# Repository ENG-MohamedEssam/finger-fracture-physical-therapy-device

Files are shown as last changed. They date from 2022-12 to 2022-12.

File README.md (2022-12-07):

# finger-fracture-physical-therapy-device

#### Note that this whole project was made by me from the Reverse-Engineering phase to the design to the fabrication of the final product

## **Abstract**

#### This project was for helping the physical therapist to help aid the patiets that had a broken or fractured finger
#### The device mainly uses a potentiometer to send the data of the the finger's angle to LCD and to the phone through a bluetooth module
#### The device has Arduino Nano as it's main controller, Potentiometer to send the Angle Data, LCD to show the data, Bluetooth module to send the data to the phone , 2 push buttons one for the hold of the readings, the second is for getting the angles in degree and minute format

#### The project went throgh four phases

## Phase 1 Idea
#### The idea was to replicate the behaviour of a digital protractor device that was already in the market to invent something that may help the patients with broken fingers
## Phase 2 Reverse-Engineering
#### So i started Reverse-Engineering the Digital protractor as shown below 
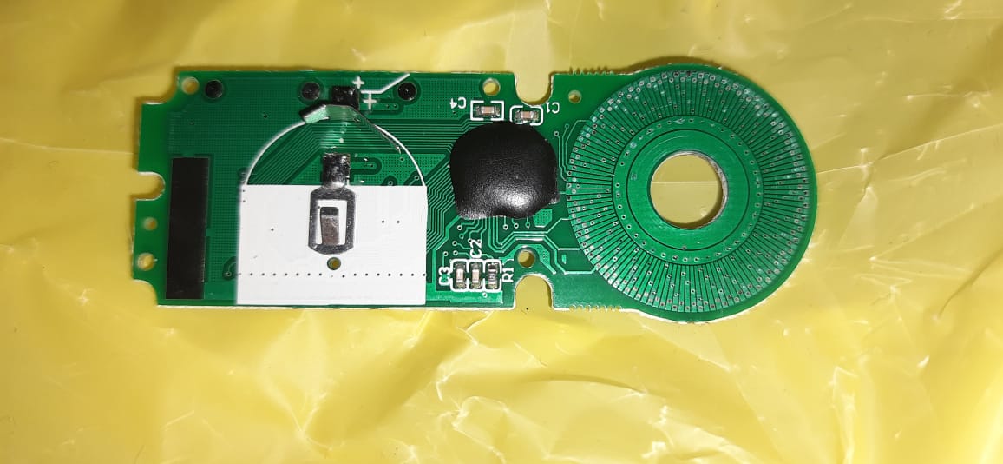
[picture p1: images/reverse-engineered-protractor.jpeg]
protractor

#### When i understood it's behaviour i started to find similar components in the Egyptian market 
#### the components that i didn't find was the induction encoder so i had to find a replacement
#### i thought of three things, Potentiometer, Normal Encoder, IMU
#### I even wrote codes for the three sesors.
## Problems 
#### IMU was too expensive for such a project but it kind of worked correctly
#### The encoders in Egypt had too little pulses so the error in Degrees was not acceptable
#### The potentiometer was the cheapest sensor so in mass production that was the ideal choice but it gave an error in the reading as well that was not acceptable and the Arduino Nano was only 10 bits in ADC

## Scenario to fix the Potentiameter's problem
#### To fix the problem in the potentiometer there were two solutions either i use the algorithm over sampling and decimation or i use the sliding window filter
#### so i went along with the over sampling and decimation technique, it was by having many readings in an array then get the average of it many times, that makes the reading more accurate.
#### The error after that algorithm was +/- 0.02 and that was more than acceptable.

## Phase 3 Design
#### In this phase i started to design the circuit on protues such as follows
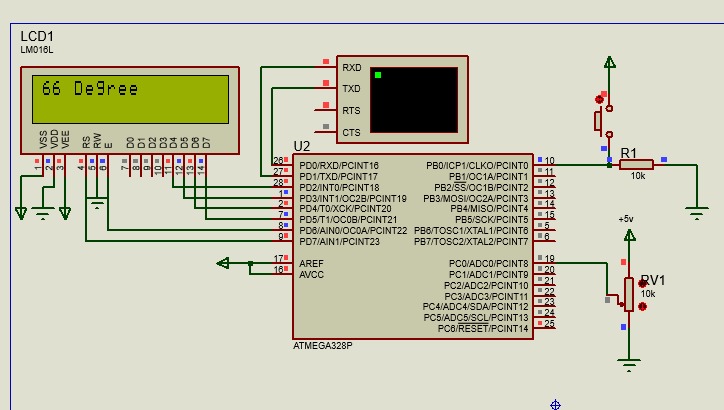
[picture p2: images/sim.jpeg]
sim

#### After i made sure it works fine i turned to try the components connections on a bread board as follows 
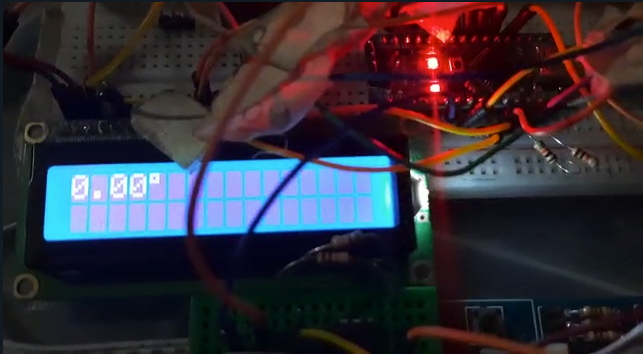
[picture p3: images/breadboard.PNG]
breadboard

#### Then i designed the circuit on Eagle-Cad program 
#### I even designed one of the three parts on SolidWorks as you can see below 
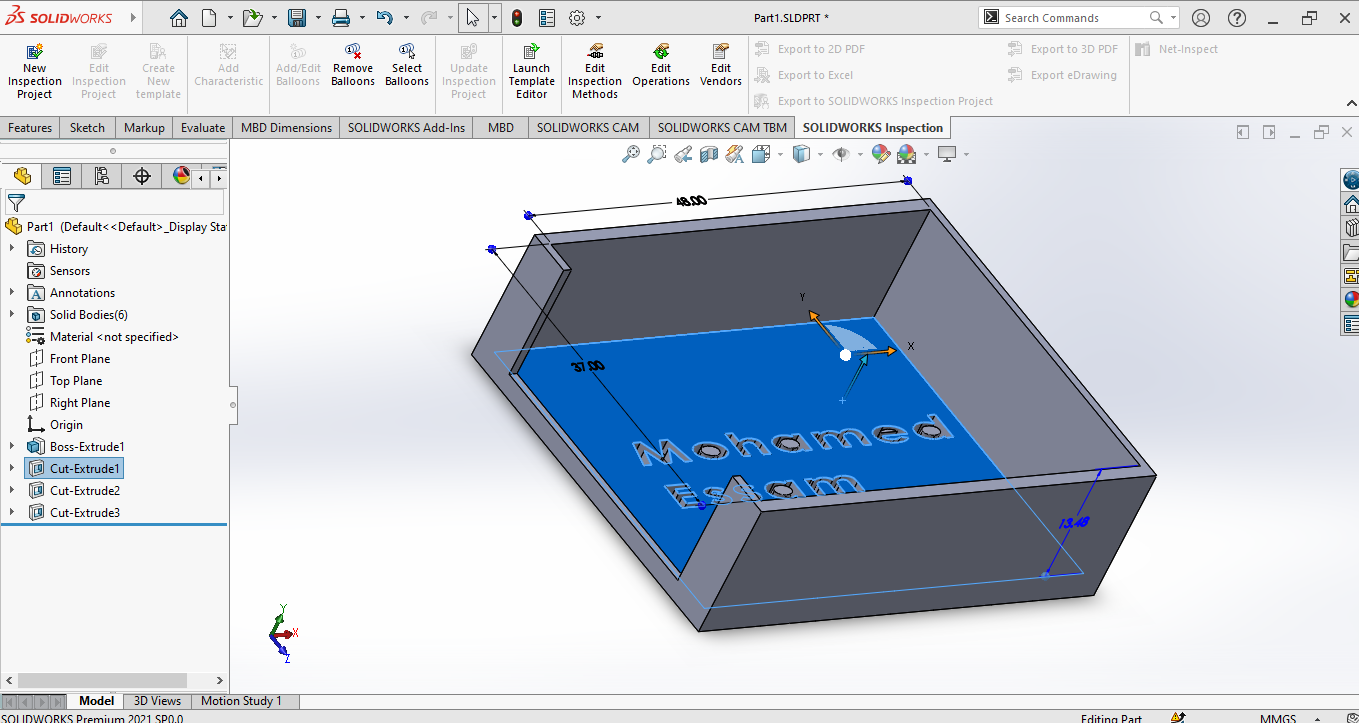
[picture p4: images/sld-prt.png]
Part

#### the other two parts were open source 

## Phase 4 fabrication
#### in this phase i fabricated the PCB and tested it and it worked fine, below are some images of the final product (The band)
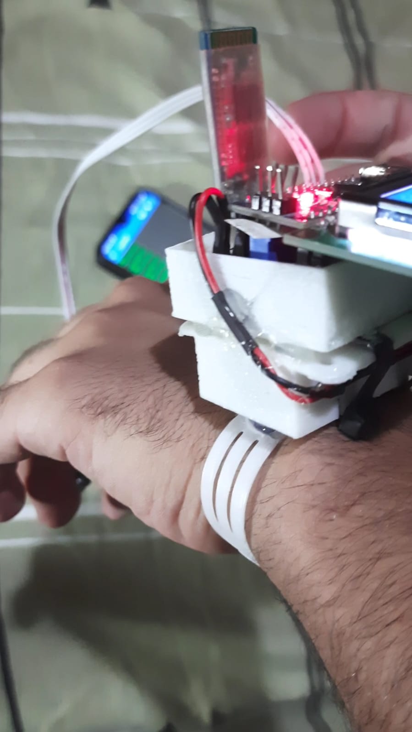
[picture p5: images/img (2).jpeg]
band-img1

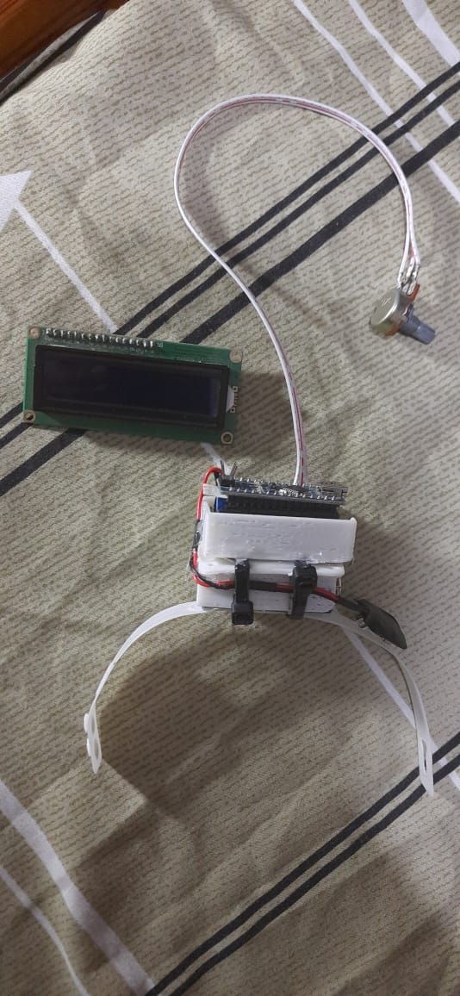
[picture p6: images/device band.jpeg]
band-img2

#### The following is a video of me explaining how the whole process works
[Explanation](https://drive.google.com/drive/folders/1u0ruocD8NN2b_IU45vWWJVkj_FHNx0_M?usp=share_link)

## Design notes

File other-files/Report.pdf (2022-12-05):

# Finger Fracture Physical Therapy Device

# Report

Name : Mohamed Essam Abd Elfattah Ibrahim.
ID : 148
Department : Electrical Power and Machines Engineering.

## This project was made under the supervision of :

## Dr. May Youssef

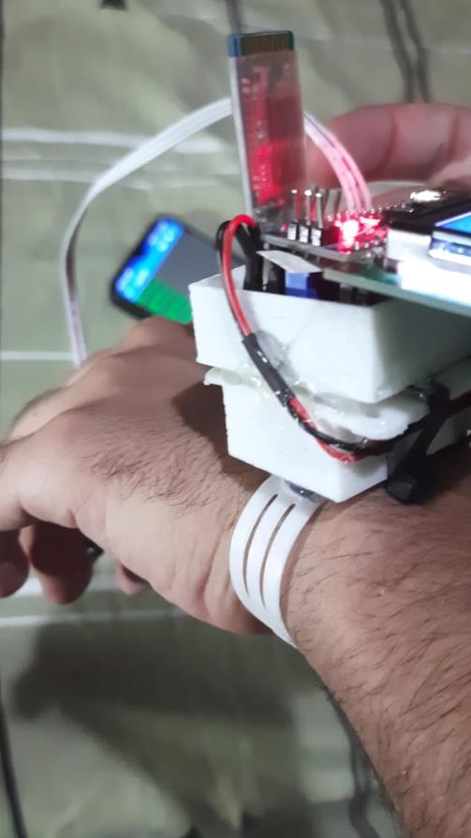
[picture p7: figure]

## Dr. Mohamed Elhabrouk

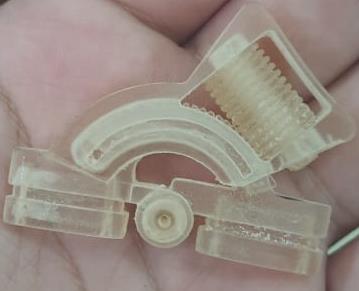
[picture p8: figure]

## Idea :

The main idea of the project was to replicate the functionality of a Digital Protractor to use it as a Physical Therapy device, by enhancing its behavior and precision in order to use it in the medical field.

## Functionality:

It’s used for physical therapy on figure fractures, It helps the Physical Therapist to read the angle and that helps him to treat the patient effectively.

## Progress:

First was the reverse Engineering process

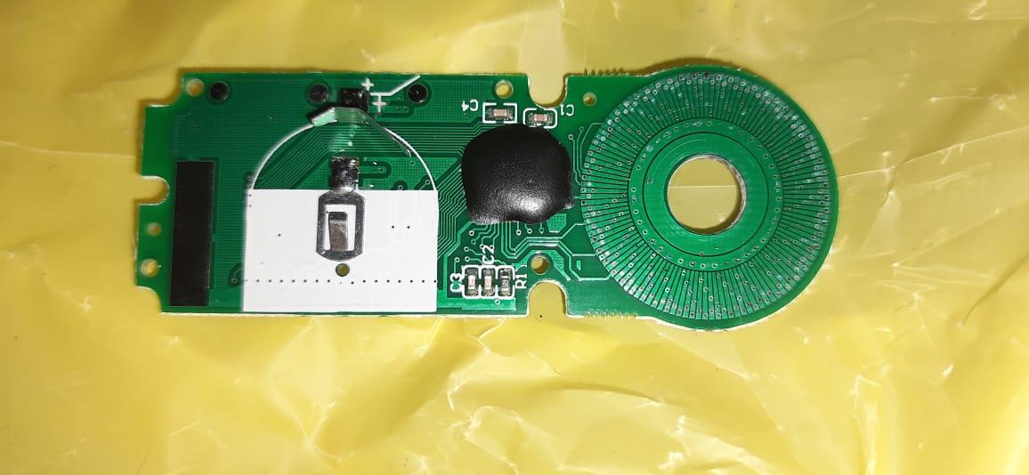
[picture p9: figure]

I was able to find out the inputs and outputs of the Digital Protractor and every sensor and component used to make it.
The main components that were inside the Digital Protractor :
- Micro-Controller
- 5 Bit LCD screen
- Inductive Position Encoder
- Switches
- 3v Battery

The main components which I used were :

- Micro-Controller (Arduino Nano)
- 16x2 LCD character screen
- Bluetooth Module (HC-05)

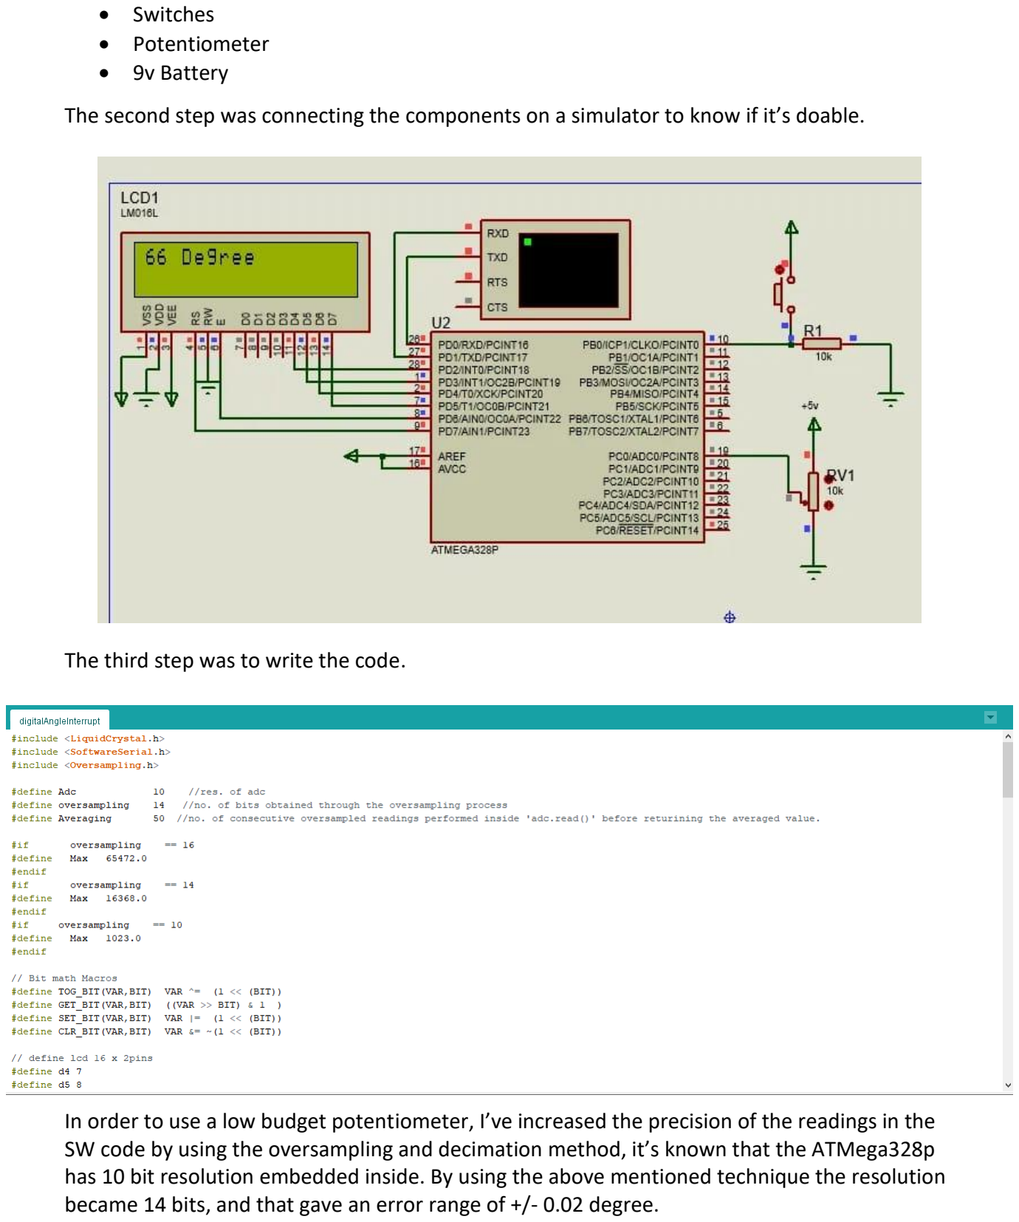
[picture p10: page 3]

- Switches
- Potentiometer
- 9v Battery

The second step was connecting the components on a simulator to know if it’s doable.

The third step was to write the code.

In order to use a low budget potentiometer, I’ve increased the precision of the readings in the SW code by using the oversampling and decimation method, it’s known that the ATMega328p has 10 bit resolution embedded inside. By using the above mentioned technique the resolution became 14 bits, and that gave an error range of +/- 0.02 degree.

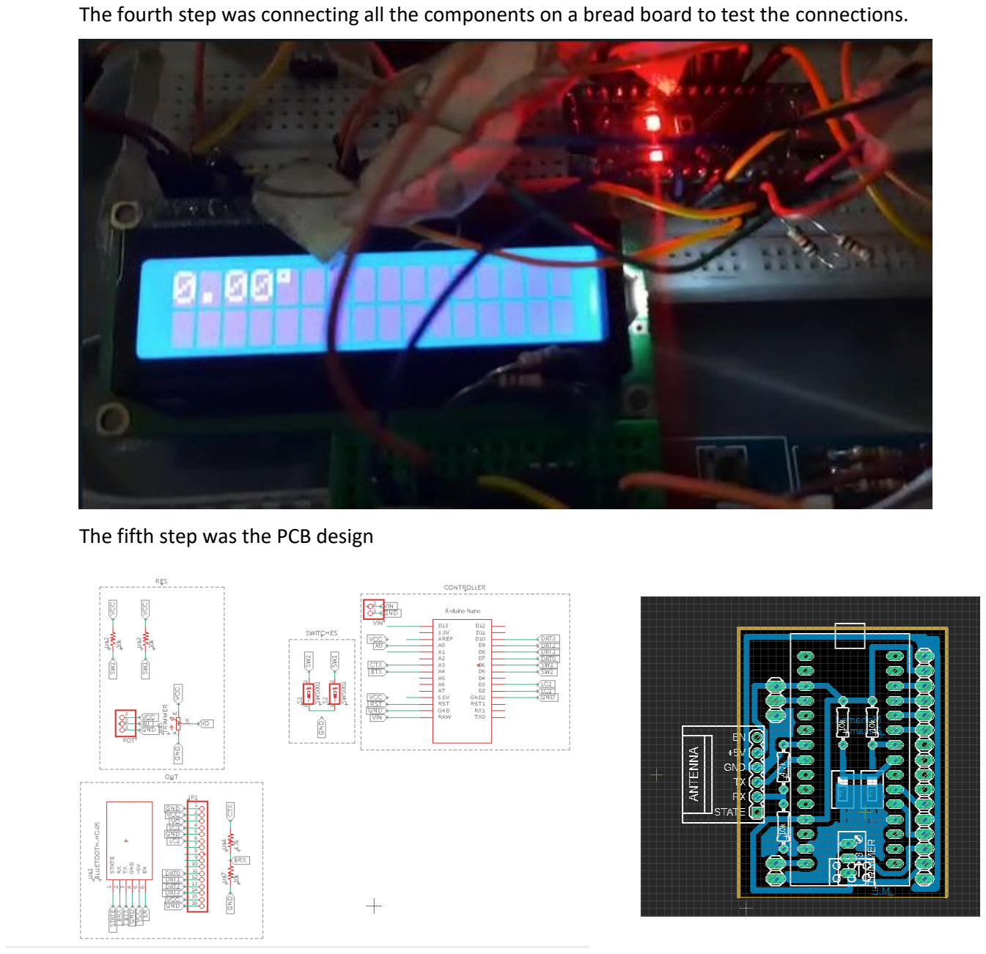
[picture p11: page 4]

The fourth step was connecting all the components on a bread board to test the connections.

The fifth step was the PCB design

The Last step was to fabricate the PCB and connect all the components on it to make it compact.

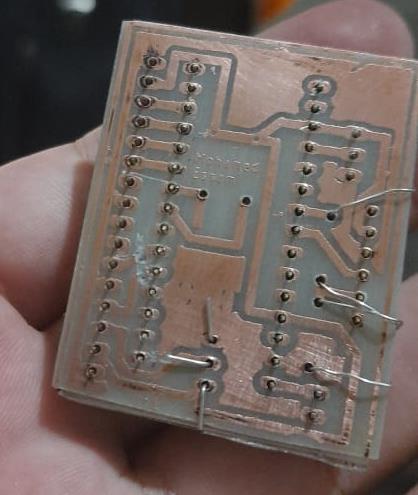
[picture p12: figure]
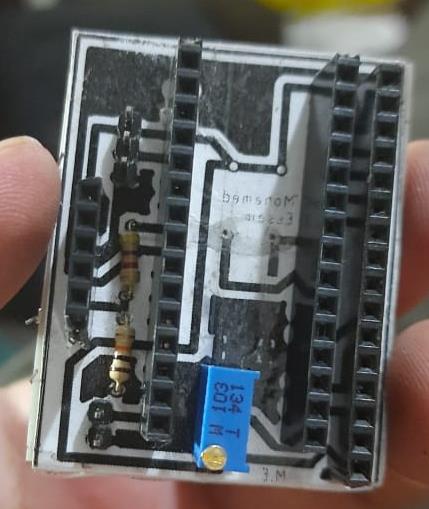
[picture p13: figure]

The final Product was a fully functioning PCB as shown in the figure below :

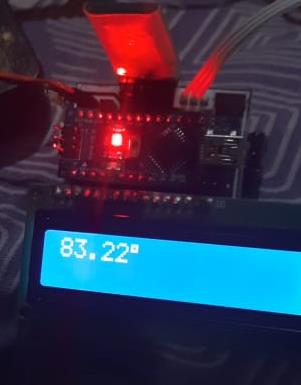
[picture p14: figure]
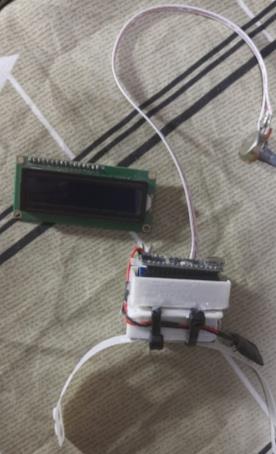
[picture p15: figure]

And by adding 3d printed parts the project became as shown:

## Features :

The project has many features, such as :

The precision that was mentioned before.

It sends the reading to an LCD and through Bluetooth module into any Bluetooth serial terminal Application on the mobile phone.

It has a switch that can Hold the reading.

Also another switch that toggles between the reading in degree with fraction and the reading in degrees and minutes.

It has a low cost Potentiometer.

It has a small sized PCB that can be put on the hand like a wrist-band.

## Future Improvements:

- Using ATMEGA328p Controller’s Chip instead of the full Nano Platform
- Using a smaller sized Bluetooth-Module
- Using a 4 digit LCD instead of 16x2 LCD to make it smaller
- Using a better quality Potentiometer
- Using a rechargeable small sized LI-PO Battery

## Notes:

The Potentiometer used is a low quality one, that’s why the Angle may be shifted by 2 to 5 degrees from the real angle depending on the potentiometer, and that can be fixed in the code using the mapping function and by getting a better-quality Potentiometer.

# Bill of Materials (BOM)

Component | Price | Quantity | Total Price | Link
Arduino Nano | 175 | 1 | 175 | https://makerselectronics.com/product/arduino-nano
16x2 LCD | 50 | 1 | 50 | https://makerselectronics.com/product/16x2-character-lcd
Bluetooth Module | 160 | 1 | 160 | https://makerselectronics.com/product/bluetooth-module-hc-05

PCB | 6 | 1 | 6 | https://makerselectronics.com/product/pcb-board-fiber
Trimmer | 3.5 | 1 | 3.5 | https://makerselectronics.com/product/multi-turn-pot-20k
Pot | 3 | 1 | 3 | https://makerselectronics.com/product/pot-1m
Switches | 1 | 2 | 2 | https://makerselectronics.com/product/push-button-3x6x5-0mm
Resistors | 0.1 | 4 | 0.4 | https://makerselectronics.com/product/resistor-1-2ohm-1-2w
9v Battery 6F22 | 15 | 1 | 15 | https://makerselectronics.com/product/camelion-battery-9v-6f22
Battery Cap | 1.5 | 1 | 1.5 | https://makerselectronics.com/product/battery-9v-cap
Pin header female | 3 | 2 | 6 | https://makerselectronics.com/product/pin-headers-female-40-pins
Pin header male | 2 | 1 | 2 | https://makerselectronics.com/product/pin-headers-male-40-pins
Data Cable 3 pin | 5.5 | 1 | 5.5 | https://makerselectronics.com/product/data-cable-jst-3-pin-30cm
19 grams of filament PLA+ | -- | -- | --

# Project Total Cost : 429.9 EGP

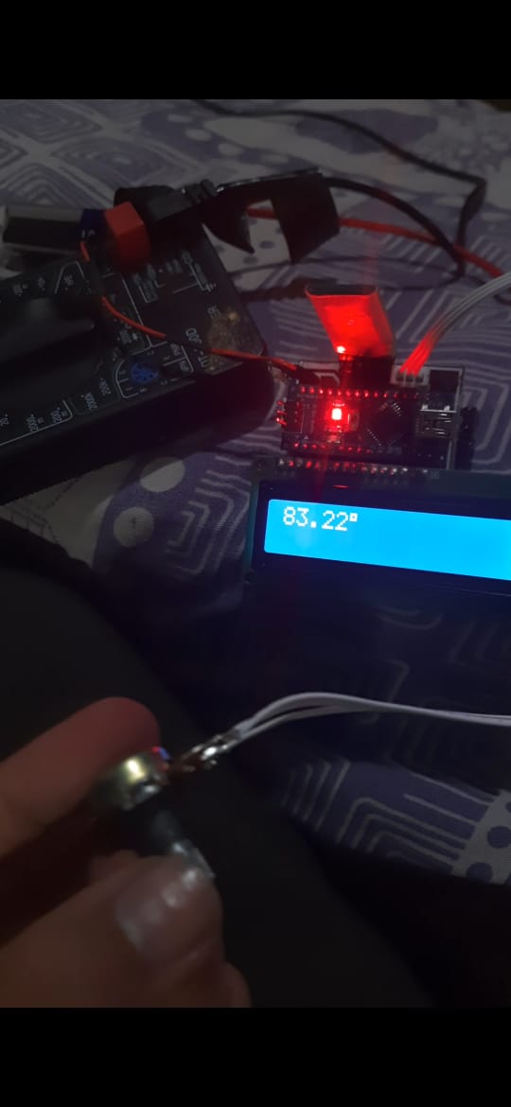
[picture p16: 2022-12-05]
images/device.jpeg

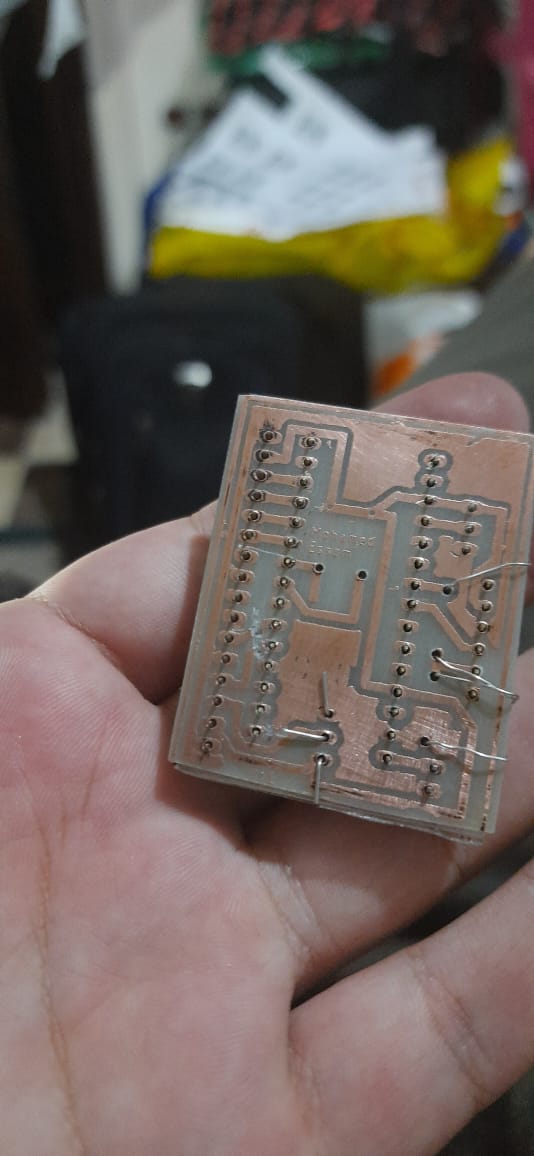
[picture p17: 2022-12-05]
images/board-bottom.jpeg

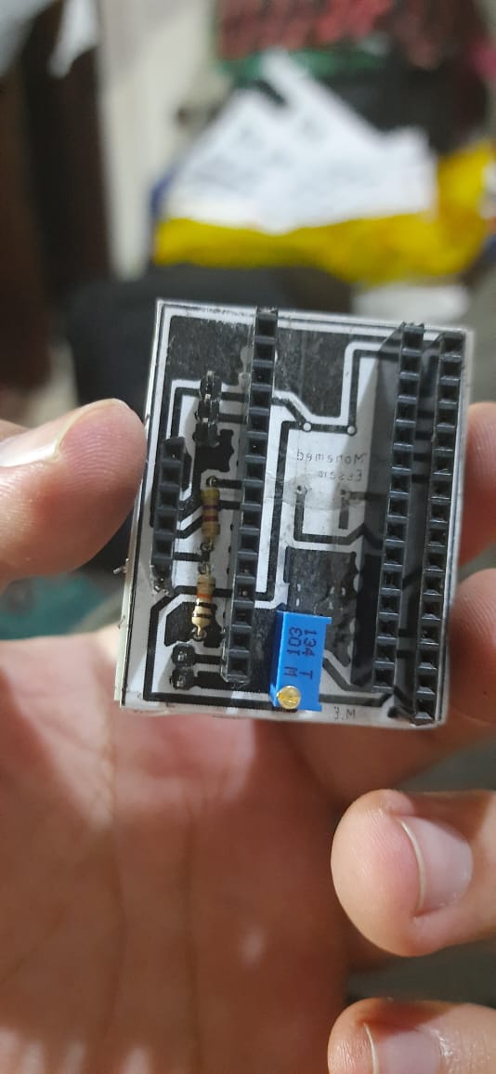
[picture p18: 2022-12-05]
images/board-top.jpeg

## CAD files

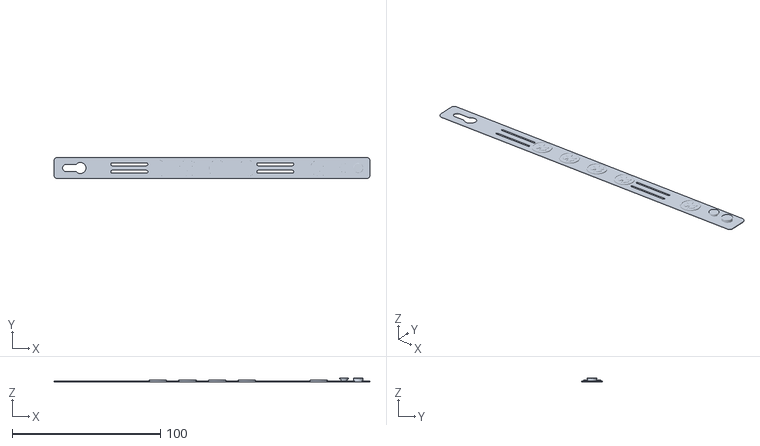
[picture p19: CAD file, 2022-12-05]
other-files/03-Band.stl
213.1 x 14.0 x 2.87

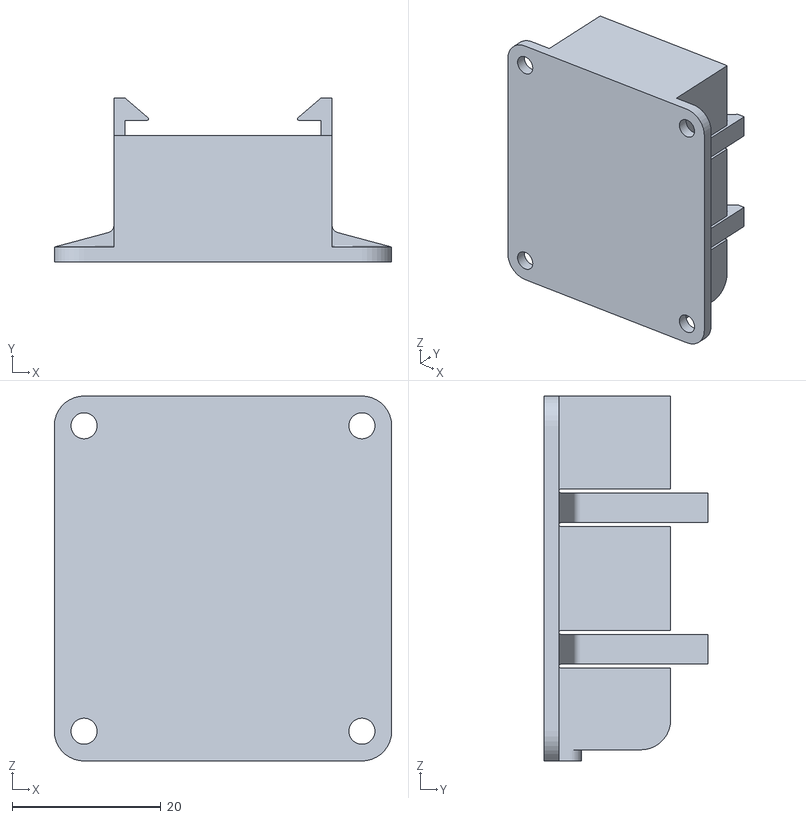
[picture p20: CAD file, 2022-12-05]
other-files/02-9VBatHolder.STL
45.3 x 22.0 x 49.0

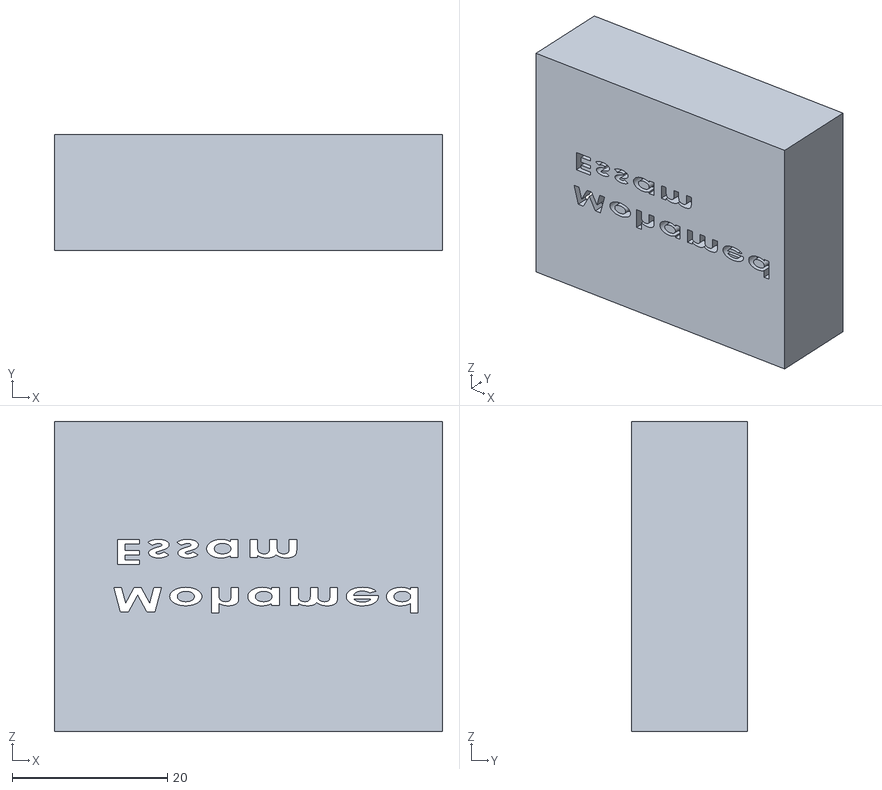
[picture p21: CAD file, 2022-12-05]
other-files/01-BrdHolder.STL
50.0 x 15.0 x 40.0

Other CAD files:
other-files/BrdHolder.SLDPRT

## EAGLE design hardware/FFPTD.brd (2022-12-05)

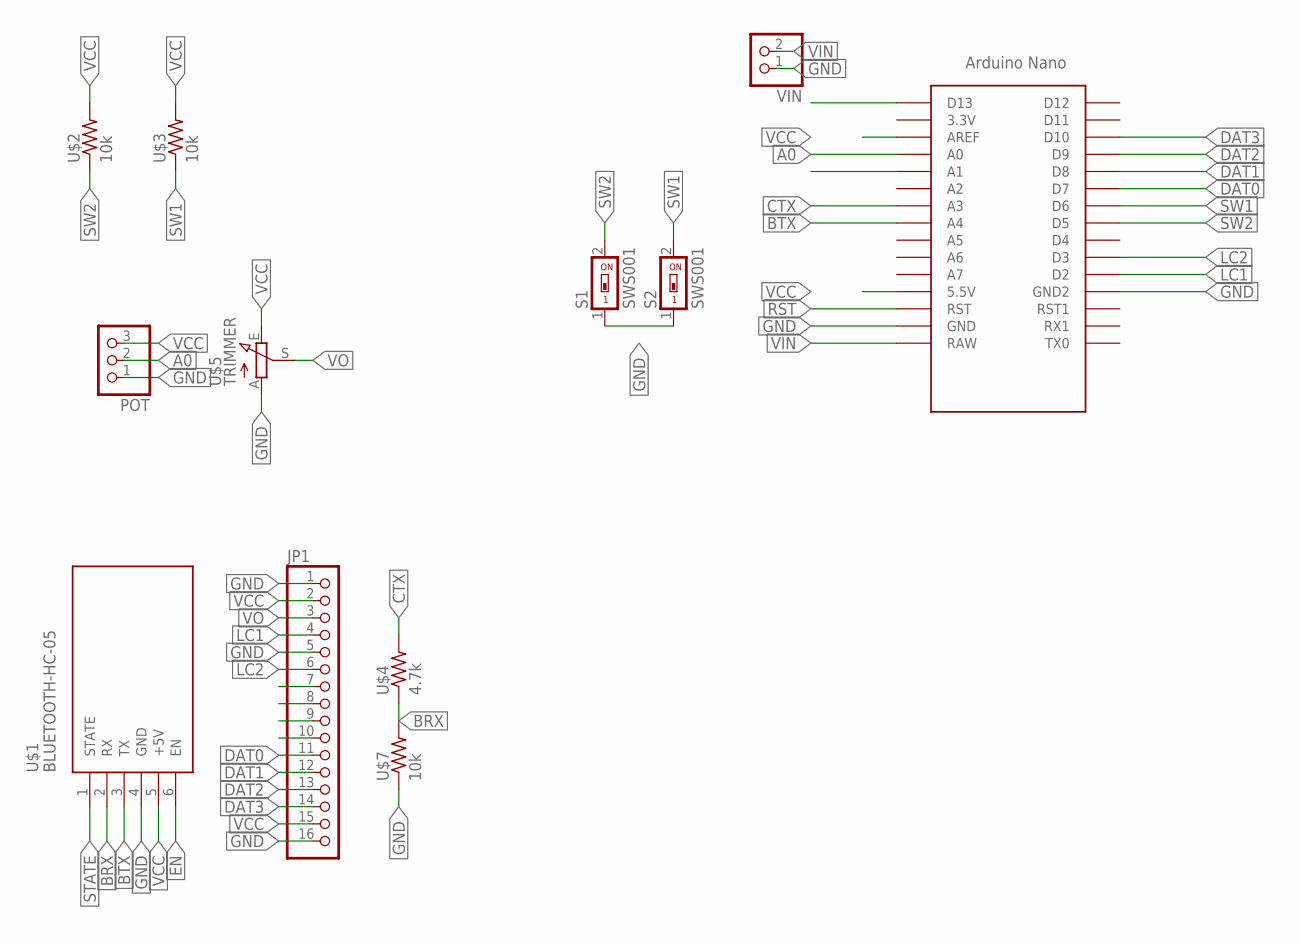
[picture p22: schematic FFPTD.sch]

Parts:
JP1: PINHD-1X16; 1X16
POT: PINHD-1X3; 1X03
S1, S2: SWS001; SMS-001
U$1: BLUETOOTH-HC-05; WIRELESS-BLUETOOTH-HC-05
U$2, U$3, U$7: 10k; 0204/7
U$4: 4.7k; 0204/7
U$5: TRIMMER; RJ9W
U$6: ARDUINO_NANO; NANO
VIN: PINHD-1X2; 1X02

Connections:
A0: POT.2, U$6.A0
BRX: U$1.2 (RX), U$4.1, U$7.2
BTX: U$1.3 (TX), U$6.A4
CTX: U$4.2, U$6.A3
DAT0: JP1.11, U$6.D7
DAT1: JP1.12, U$6.D8
DAT2: JP1.13, U$6.D9
DAT3: JP1.14, U$6.D10
EN: U$1.6 (EN)
GND: JP1.1, JP1.5, JP1.16, POT.1, S1.1, S2.1, U$1.4 (GND), U$5.A, U$6.GND, U$6.GND1 (GND2), U$7.1, VIN.1
LC1: JP1.4, U$6.D2
LC2: JP1.6, U$6.D3
RST: U$6.RST
STATE: U$1.1 (STATE)
SW1: S2.2, U$3.1, U$6.D6
SW2: S1.2, U$2.1, U$6.D5
VCC: JP1.2, JP1.15, POT.3, U$1.5 (+5V), U$2.2, U$3.2, U$5.E, U$6.5V (5.5V), U$6.AREF
VIN: U$6.RAW, VIN.2
VO: JP1.3, U$5.S

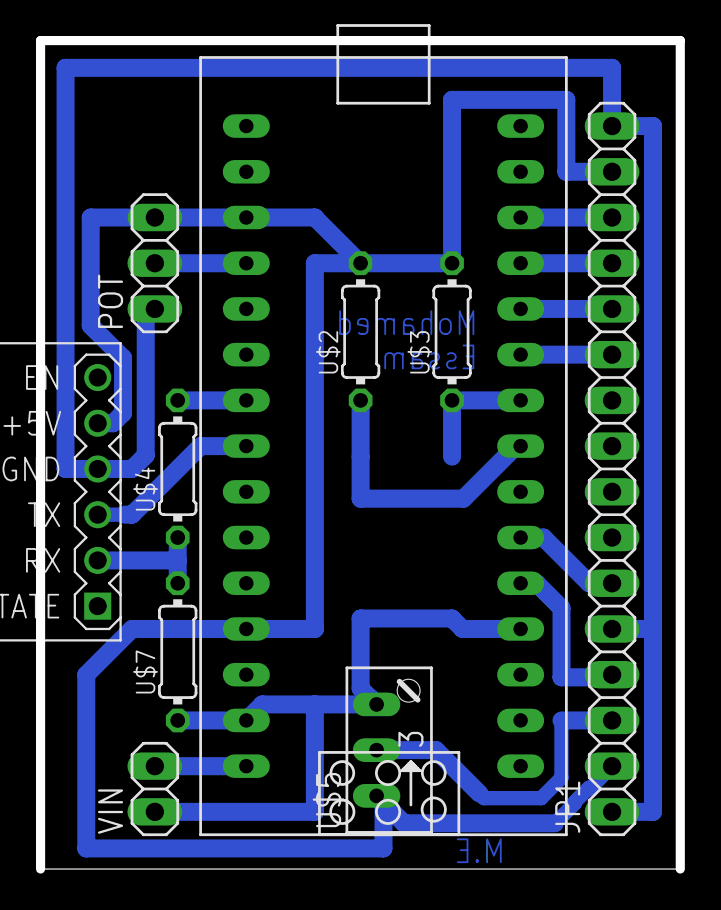
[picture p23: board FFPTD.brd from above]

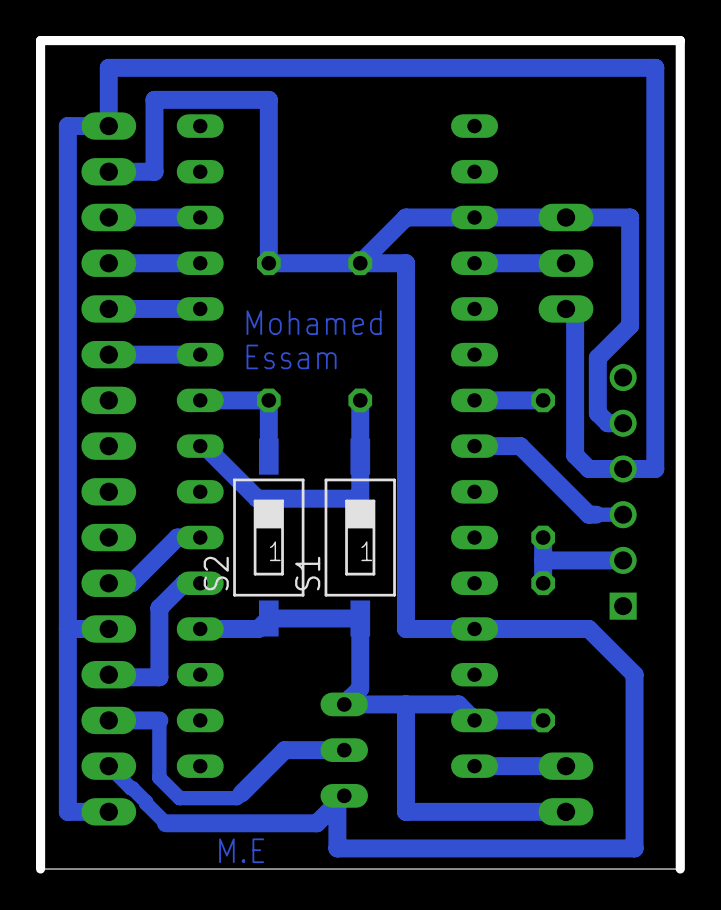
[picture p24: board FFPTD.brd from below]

Board: 2 copper layers, 35.5 x 46.0 mm, 12 parts (2 on the bottom side), 16 nets.

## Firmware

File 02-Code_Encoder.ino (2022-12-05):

#include <LiquidCrystal.h>
#include <SoftwareSerial.h>

// Bit math macros 
#define TOG_BIT(VAR,BIT)  VAR ^=  (1 << (BIT))
#define GET_BIT(VAR,BIT)  ((VAR >> BIT) & 1  )
#define SET_BIT(VAR,BIT)  VAR |=  (1 << (BIT))
#define CLR_BIT(VAR,BIT)  VAR &= ~(1 << (BIT))

// define lcd 16 x 2pins 
#define d4 A4
#define d5 A3
#define d6 A2
#define d7 A1
#define en 6 
#define rs 7

// Switches 
#define  Hold   10
#define  D_M    11

// Analog read from pot
//#define  A0     8 

// Bluetooth Module
#define TxD 8
#define RxD 9

#define PinA  4
#define PinB  3

#define degree_symbol "\337"

//float adcVal,angle;
float degree,minute;
char Flag = 3;

int aVal;
int PinALast;
int EncoderPosCount = 0;

float angle;

LiquidCrystal lcd(rs, en, d4, d5, d6, d7);
SoftwareSerial mySerial(RxD, TxD); 

void FLAG_VAL(void);
float mapf(float x, float in_min, float in_max, float out_min, float out_max);


void setup() {

  //pinMode(A0,INPUT);

  pinMode (PinA,INPUT);
  pinMode (PinB,INPUT);
  
  pinMode(Hold,INPUT);
  pinMode(D_M,INPUT);
  
  // Initialization
  Serial.begin(9600);
  mySerial.begin(9600);
  lcd.begin(16, 2);
  lcd.setCursor(0,0);
  
  PinALast = digitalRead(PinA); // Read Pin A Initial State
  attachInterrupt(digitalPinToInterrupt(PinB), update, CHANGE);

}

void loop() {
  angle = mapf(EncoderPosCount,0.00,30.00,0.00,360.00); // mapping float values from analog to pot values
 // angle = (float)EncoderPosCount;
  FLAG_VAL(); // call function to check flags 

  if(!GET_BIT(Flag,0)) // if D/M is pressed once 
  {
    degree = angle;
    minute = (angle - (int)degree ) * 60.0;
    // Print values to LCD
    lcd.print((int)degree);
    lcd.print(degree_symbol);
    lcd.print((int)minute);
    lcd.print("'");
    // Print values to serial monitor 
    Serial.println(" ");
    Serial.println("******* Value *******");
    Serial.print((int)degree);
    Serial.print("°");
    Serial.print((int)minute);
    Serial.print("'");
    Serial.println(" ");
    Serial.println("*********************");
    // Print values to BTM ( Bluetooth Module )
    mySerial.println(" ");
    mySerial.println("******* Value *******");
    mySerial.print(degree);
    mySerial.print("°");
    mySerial.print(minute);
    mySerial.print("'");
    mySerial.println(" ");
    mySerial.println("*********************");
    }
  else // (digitalRead(D_M) == 1) // if D/M pressed again
  {
    // Print values to LCD
    lcd.print(angle);
    lcd.print(degree_symbol);
    // Print values to Serial Monitor 
    Serial.println(" ");
    Serial.println("******* Value *******");
    Serial.print(angle);
    Serial.print("°");
    Serial.print(" ");
    Serial.println(" ");
    Serial.println("*********************");
    // Print values to BTM
    mySerial.println(" ");
    mySerial.println("******* Value *******");
    mySerial.print(angle);
    mySerial.print("°");
    mySerial.print(" ");
    mySerial.println(" ");
    mySerial.println("*********************");
  }
  
  while(!GET_BIT(Flag,1)) // If Hold is pressed 
  {
    FLAG_VAL(); // Keep checking the change in flags 
    if(GET_BIT(Flag,2))
    {
      Serial.print('H');
      lcd.print('H');
    }
    CLR_BIT(Flag,2);
    delay(100);

    };

 // delay(500);
  lcd.clear();
  lcd.setCursor(0,0);
}


void FLAG_VAL(void)
{
  if(!digitalRead(D_M))
  {
    TOG_BIT(Flag,0);
    delay(300);
  }
  if(!digitalRead(Hold))
  {
    TOG_BIT(Flag,1);
    SET_BIT(Flag,2);
    delay(300);
  }
}

// Function for mapping 
float mapf(float x, float in_min, float in_max, float out_min, float out_max)
{
  return (x - in_min) * (out_max - out_min) / (in_max - in_min) + out_min;
}


void update ()
{
    aVal = digitalRead(PinA); // Reads the "current" state of the outputA
  // If the previous and the current state of the outputA are different, that means a Pulse has occured

    if(aVal != PinALast) // if Pin A value doesn't equal last pos 
  // If the outputB state is different to the outputA state, that means the encoder is rotating clockwise
  {
    if(digitalRead(PinB) != aVal) // Rotating CW
    {
      EncoderPosCount ++;
    }
    else
    {
      EncoderPosCount --;
    }
  }
    PinALast = aVal;
}

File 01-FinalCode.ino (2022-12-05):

#include <LiquidCrystal.h>
#include <SoftwareSerial.h>
#include <Oversampling.h>

#define Adc             10    //res. of adc
#define oversampling    14   //no. of bits obtained through the oversampling process
#define Averaging       50  //no. of consecutive oversampled readings performed inside 'adc.read()' before returining the averaged value.

#if       oversampling    == 16
#define   Max   65472.0
#endif 
#if       oversampling    == 14
#define   Max   16368.0
#endif
#if     oversampling    == 10
#define   Max   1023.0
#endif

// Bit math Macros 
#define TOG_BIT(VAR,BIT)  VAR ^=  (1 << (BIT))
#define GET_BIT(VAR,BIT)  ((VAR >> BIT) & 1  )
#define SET_BIT(VAR,BIT)  VAR |=  (1 << (BIT))
#define CLR_BIT(VAR,BIT)  VAR &= ~(1 << (BIT))

// define lcd 16 x 2pins 
#define d4 7
#define d5 8
#define d6 9
#define d7 10
#define en 6
#define rs 5

// Switches 
#define  Hold   3
#define  D_M    2

//Analog read from pot
#define  A0     8 

//BTM SWSerial 
#define TxD 11
#define RxD 12

#define degree_symbol "\337"

// Vars
float adcVal,angle;
float degree,minute;
char Flag = 3;

LiquidCrystal lcd(rs, en, d4, d5, d6, d7);
SoftwareSerial mySerial(RxD, TxD); 
Oversampling  adc(Adc, oversampling, Averaging);


void PrintValues(void); // Print fun
void UpdateHold(void);
void UpdateD_M(void);
float mapf(float x, float in_min, float in_max, float out_min, float out_max); // float map fun


void setup() {
  
  pinMode(Hold,INPUT);
  pinMode(D_M,INPUT);
  
  // Initialization
  Serial.begin(9600);
  mySerial.begin(9600);
  lcd.begin(16, 2);
  lcd.setCursor(0,0);

  attachInterrupt(digitalPinToInterrupt(Hold) , UpdateHold , FALLING );
  attachInterrupt(digitalPinToInterrupt(D_M ) ,UpdateD_M  , FALLING );
}

void loop() {
  adcVal = adc.read(0);
  angle = mapf(adcVal,0.0,Max,0.0,270.0); // mapping float values from analog to pot values 
  PrintValues();
}

void PrintValues(void)
{
      lcd.clear();
      lcd.setCursor(0,0);
      if(!GET_BIT(Flag,0)) // if D/M is pressed once 
    {
      degree = angle;
      minute = (angle - (int)degree ) * 60.0;
      // Print values to LCD
      lcd.print((int)degree);
      lcd.print(degree_symbol);
      lcd.print((int)minute);
      lcd.print("'");
      // Print values to serial monitor 
      Serial.println(" ");
      Serial.println("******* Value *******");
      Serial.print((int)degree);
      Serial.print("°");
      Serial.print((int)minute);
      Serial.print("'");
      Serial.println(" ");
      Serial.println("*********************");
      // Print values to BTM ( Bluetooth Module )
      mySerial.println(" ");
      mySerial.println("******* Value *******");
      mySerial.print((int)degree);
      mySerial.print("°");
      mySerial.print((int)minute);
      mySerial.print("'");
      mySerial.println(" ");
      mySerial.println("*********************");
      }
    else // (digitalRead(D_M) == 1) // if D/M pressed again
    {
      // Print values to LCD
      lcd.print(angle);
      lcd.print(degree_symbol);
      // Print values to Serial Monitor 
      Serial.println(" ");
      Serial.println("******* Value *******");
      Serial.print(angle);
      Serial.print("°");
      Serial.print(" ");
      Serial.println(" ");
      Serial.println("*********************");
      // Print values to BTM
      mySerial.println(" ");
      mySerial.println("******* Value *******");
      mySerial.print(angle);
      mySerial.print("°");
      mySerial.print(" ");
      mySerial.println(" ");
      mySerial.println("*********************");
    }
    
    while(!GET_BIT(Flag,1)) // If Hold is pressed 
    {
      if(GET_BIT(Flag,2))
      {
        Serial.print('H');
        lcd.print('H');
      }
      CLR_BIT(Flag,2);
      delay(100);
    };
}

void UpdateHold(void)
{
  TOG_BIT(Flag,1);
  SET_BIT(Flag,2);
}
void UpdateD_M(void)
{
  TOG_BIT(Flag,0);
}

float mapf(float x, float in_min, float in_max, float out_min, float out_max)
{
  return (x - in_min) * (out_max - out_min) / (in_max - in_min) + out_min;
}
